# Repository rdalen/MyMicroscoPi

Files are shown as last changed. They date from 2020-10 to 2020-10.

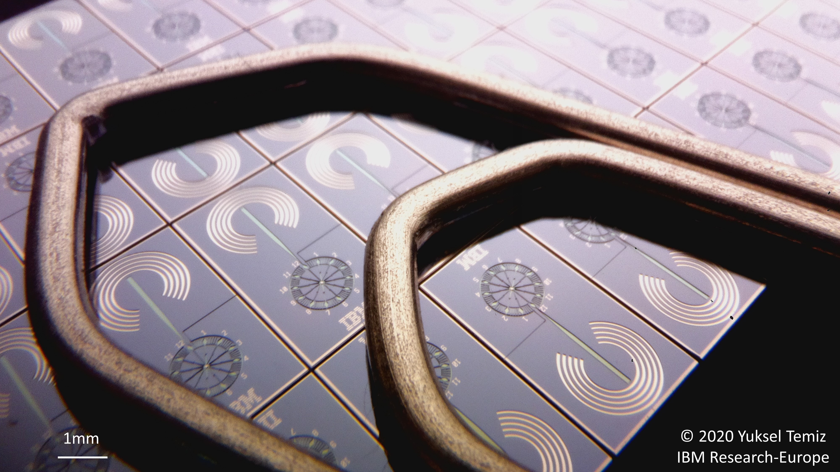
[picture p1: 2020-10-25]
Docs/Original/Image-examples/Microfluidic-clock_and_paper-clip.jpg

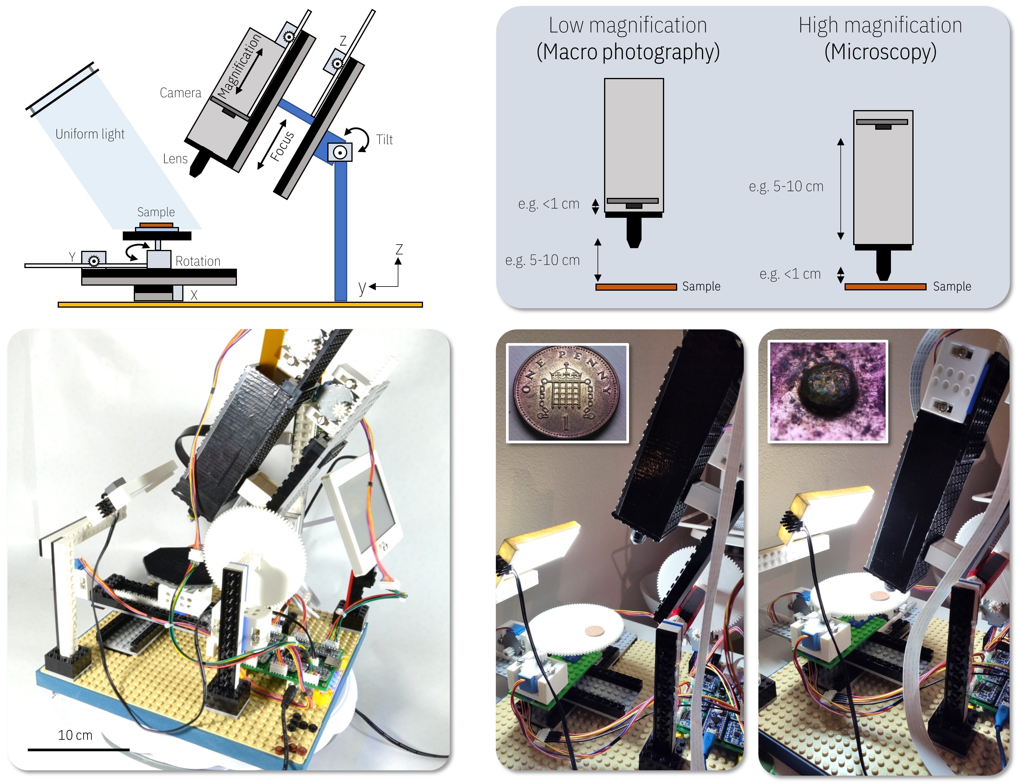
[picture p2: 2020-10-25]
Docs/Original/Pics/Operation.jpg

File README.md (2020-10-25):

# MyMicroscoPi
This DIY microscope design combines many of my hobbies; Lego, electronics, 3D printing, Arduino, Raspberry Pi, etc.

My design is a remix of a great and well documented [design of Yuksel Temizon](https://github.com/IBM/MicroscoPy).
My version is also built of LEGO bricks, but uses also LEGO Technic beams because they are light and strong.
For capturing images it uses a Raspberry Pi 3B+ with an 8MP camera and modified lens. The six stepper motors for the camera & sample movements and the power LED for illumination are controlled by two PCB's with an [Arduino Pro mini](https://www.arduino.cc/en/Guide/ArduinoProMini) on each PCB.
* One PCB (Mainboard) contains all the driver hardware for the steppers and power LED
* The other PCB (Controller board) contains the human interface elements for controlling the microscope. Such as; Three joysticks to control the X, Y, Rotary, Tilt (Camera-angle), Magnitude and Focus, a Rotary encoder to control the Power LED and a small OLED display to indicate the brightness of the power LED

I used the 3D printed LEGO gears and adapters of the [original design](https://github.com/IBM/MicroscoPy)

So, after many hours of building pleasure, I'm going to do some nice experiments now

### Information & Documentation
* [Hackster.io project; IBM Researcher Makes a Microscope Using LEGO, Arduino, and Raspberry Pi](https://www.hackster.io/news/ibm-researcher-makes-a-microscope-using-lego-arduino-and-raspberry-pi-cbc58cb69a20?utm_source=Hackster+Marketing&utm_campaign=7e2e7b20ec-EMAIL_CAMPAIGN_2019_02_14_02_53_COPY_01&utm_medium=email&utm_term=0_86d76c4d75-7e2e7b20ec-144680307&mc_cid=7e2e7b20ec&mc_eid=ea3c09e980)
* [Github IBM/MicroscoPy](https://github.com/IBM/MicroscoPy)
* [YouTube link MyMicroscoPi](https://youtu.be/3TL11zC14ig)

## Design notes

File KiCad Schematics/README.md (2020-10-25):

# KiCad
* Both PCB's are made with the version V1.0 design
* Modifications on these PCB's are incorporated in the version V2.0 schematics
* Hence; V2.0 has no PCB-update!!
* The gerber file of the Controllerboard V1.0 consists of a panel with 2 PCB's

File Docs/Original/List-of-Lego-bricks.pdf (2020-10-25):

List of Lego bricks used in the prototypes.

Some bricks may not be available in your country, but there are always alternative implementations in the world of Lego bricks. Also, there are probably many different ways of building a similar or better modules than I designed.
So, use your imagination and order extra bricks from different kinds in case you may want to modify something.

Keep in mind that some parts are required to be glued to a bigger piece for better mechanical stability.

I appreciate if you also keep in mind that this is a research prototype originated from my hobby, not a product.
There are probably many things that could have been done better, so consider the documents as a guideline but not as a product manual. Please let me know if you spot an error or have suggestions for improvements.

### https://www.lego.com/en-us/page/static/pick-a-brick

Module | Lego design name | Lego design ID | Quantity per unit | Quantity total | Purpose | Page # in the instructions | Comments
Base | 1 unit
| Baseplate 32x32 | | 1 | 1 | base | 32 | needs to be fixed to a rigid substrate
Linear actuators | 4 units
| PLATE 6X16 | 3027 | 1 | 4 | main plate for the linear stage | 5
| SLIDING PIECE 1X4 | 2653 | 8 | 32 | sliding guides on the sides | 5
| PLATE 1X2 WITH SLIDE | 32028 | 2 | 8 | sliding pieces | 7
| PLATE 2X4 | 3020 | 1 | 4 | moving plate | 7
| PLATE 2x6 | 3795 | 1 | 4 | mechanical stability | 6
| PLATE 6x8 | 3036 | 1 | 4 | motor plate | 6
| BRICK CORNER 1X2X2 | 2357 | 2 | 8 | mechanical stability | 6
| PLATE 2X4 | 3020 | 1 | 4 | motor Lego adapter | 9
Camera module | 1 unit | | | | | | in addition to one linear stage
| WALL ELEMENT 1X4X3, ABS | 60581 | 8 | 8 | sidewalls | 18
| PLATE 6X16 | 3027 | 1 | 1 | top cover | 19
| ANGLE PLATE 1X2 / 2X4 | 21731 | 1 | 1 | top cover connection | 19
| ANGULAR PLATE 1.5 BOT. 1X2 2/2 | 99207 | 1 | 1 | camera Lego adapter | 15
| PLATE 6x6 | 3958 | 1 | 1 | front cover | 19
| FRAME 1X4X3 | 60594 | 2 | 2 | Camera-Z connection spacer | 58
| PLATE 2X4 | 3020 | 1 | 1 | Camera-Z connection spacer | 57
Rotaty stage (option 1) | 1 unit
| 10x10 OCTOGONAL PLATE | 89523 | 1 | 1 | stage | 25
| PROFILE BRICK Ø15.83 W. CROSS | 92947 | 1 | 1 | connection to the motor | 25
| PLATE 2X4 | 3020 | 1 | 1 | motor Lego adapter | 25
Rotaty stage (option 2) | 1 unit | | | | | | preferred, better precision
| PLATE 4X12 | 3029 | 1 | 1 | stage base | 26
| LIGHT SWORD - BLADE | 21462 | 1 | 1 | pivot rod | 26
| NOSE CONE 2X2X2 | 14918 | 1 | 1 | support for the rod | 26
| PLATE 2X4 | 3020 | 1 | 1 | mechanical stability | 26
| PLATE 2X4 | 3020 | 1 | 1 | motor Lego adapter | 25
Vertical supports | 3 units | | | | | | tilt mechanism and illumination
| BRICK 1X16 | 2465 | 2 | 6 | pillar | 30
| PLATE 2X16 | 4282 | 1 | 3 | pillar | 30
| FRAME PLATE 4X4 | 64799 | 1 | 3 | pillar support | 30
| ANGULAR PLATE 1.5 BOT. 1X2 2/2 | 99207 | 1 | 3 | connection | 30
| BRICK CORNER 1X2X2 | 2357 | 4 | 12 | connection | 30
| PLATE 1X4 | 3710 | 4 | 12 | connection | 30
| PLATE 1x2 | 3023 | 4 | 12 | connection | 30
Tilt mechanism | 1 unit
| TECHNIC BRICK 1X2, Ø4.9 | 3700 | 2 | 2 | camera stage | 31
| CONN.BUSH W.FRIC./CROSSALE | 43093 | 2 | 2 | camera stage | 31
| PLATE 2X8 | 3034 | 2 | 2 | camera stage | 31
| BRICK 2X6 | 44237 | 1 | 1 | camera stage | 31
| PLATE 2X4 | 3020 | 3 | 3 | mechanical stability | 34-37
| PLATE 2X4 | 3020 | 1 | 1 | motor Lego adapter | 34-37
| PROFILE BRICK Ø15.83 W. CROSS | 92947 | 5 | 5 | spacer | 34-37
| TURN PLATE 2X2, LOWER PART | 3680 | 2 | 2 | rotation | 34-37
| TURN PLATE 2X2, UPPER PART | 3679 | 2 | 2 | rotation | 34-37
Illumination | 1 unit | | | | | | in addition to one vertical support
| CONN.BUSH W.FRIC./CROSSALE | 43093 | 4 | 4 | connection to the stage | 42-44 | for bottom illumination
| BRICK 1X16 | 2465 | 2 | 2 | horizontal connection | 43
| PLATE 2X16 | 4282 | 1 | 1 | horizontal connection | 43
| BRICK 2X2 W. BALL Ø 10.2 | 57909 | 1 | 1 | hinge | 43 | for top illumination
| BRICK 2X2 W. CUP FOR BALL | 92013 | 1 | 1 | hinge | 43 | for top illumination

OPTIONAL
HQ camera (experimental) | 1 unit | | | | | | Optional. Refer to the Instructions_HQ.pdf
linear actuator | PLATE 8x16 | 92438 | 1 | 1 | main plate | 4
linear actuator | PLATE 6x8 | 3036 | 1 | 1 | motor plate | 4
linear actuator | PLATE 2x8 | 3034 | 1 | 1 | mechanical stability | 4
linear actuator | PLATE 2x6 | 3795 | 1 | 1 | moving plate | 4 | same as camera v2
linear actuator | PLATE 1X2 WITH SLIDE | 32028 | 2 | 2 | sliding pieces | 4 | same as camera v2
linear actuator | BRICK CORNER 1X2X2 | 2357 | 2 | 2 | mechanical stability | 4 | same as camera v2
linear actuator | PLATE 2X4 | 3020 | 1 | 1 | motor Lego adapter | 4 | same as camera v2
linear actuator | SLIDING PIECE 1X4 | 2653 | 8 | 8 | sliding guides on the sides | 4 | same as camera v2
camera module | ANGULAR PLATE 1.5 BOT. 1X2 2/2 | 99207 | 1 | 1 | camera Lego adapter | 6 | same as camera v2
camera module | PLATE W. BOW 2X2X2/3 | 15068 | 1 | 1 | mechanical stability | 7
camera module | WALL ELEMENT 1X4X3, ABS | 60581 | 8 | 8 | sidewalls | 9 | same as camera v2
camera module | BRICK 1X16 | 2465 | 4 | 4 | additional height | 9
camera module | ANGLE PLATE 1X2 / 2X4 | 21731 | 1 | 1 | top cover connection | 10 | same as camera v2
camera module | PLATE 8X16 | 92438 | 1 | 1 | top cover | 10
camera module | PLATE 8X8 | 41539 | 1 | 1 | front cover | 10
tilt mechanism | PLATE 4X8 | 3035 | 2 | 2 | camera stage top and bottom plate | 13 | wider stage
tilt mechanism | TECHNIC BRICK 1X2, Ø4.9 | 3700 | 2 | 2 | camera stage | 13 | same as camera v2
tilt mechanism | CONN.BUSH W.FRIC./CROSSALE | 43093 | 2 | 2 | camera stage | 13 | same as camera v2
tilt mechanism | BRICK 1X8 | 3008 | 2 | 2 | camera stage | 13
tilt mechanism | PLATE 2X6 | 3795 | 1 | 1 | camera stage | 13

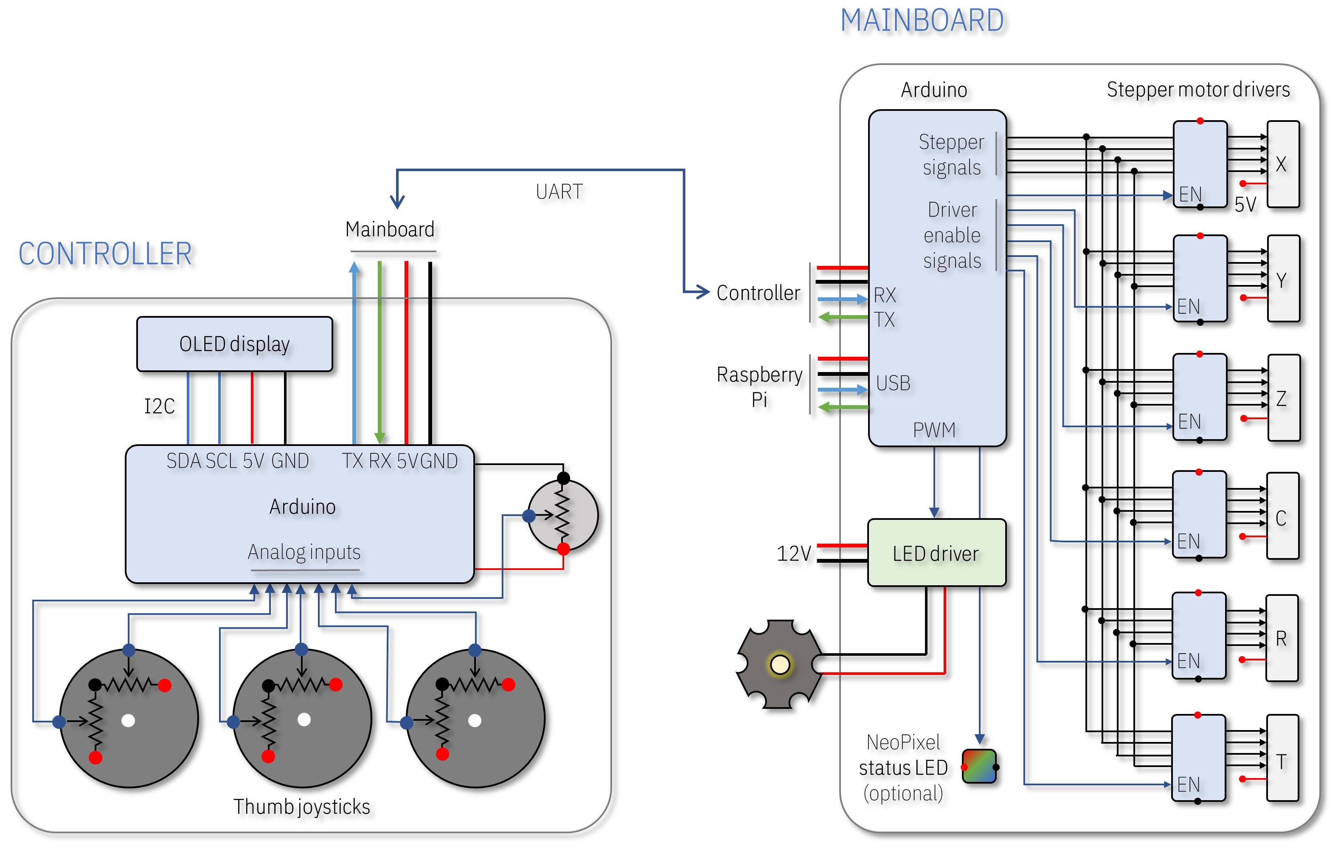
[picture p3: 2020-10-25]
Docs/Original/Pics/Electronics.jpg

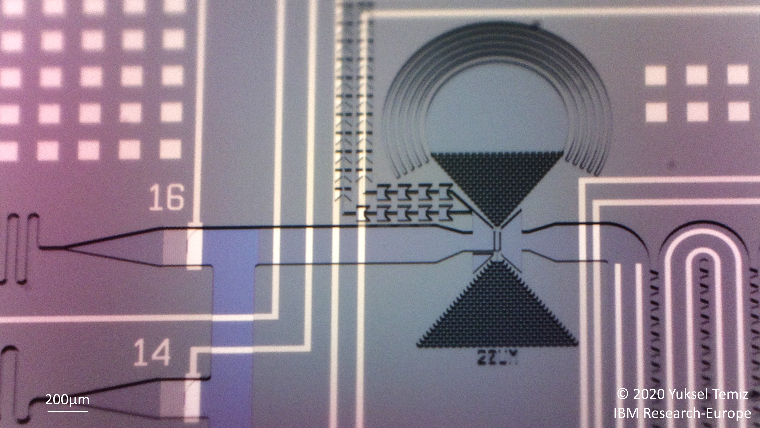
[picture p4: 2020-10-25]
Docs/Original/Image-examples/Microfluidic-structures.jpg

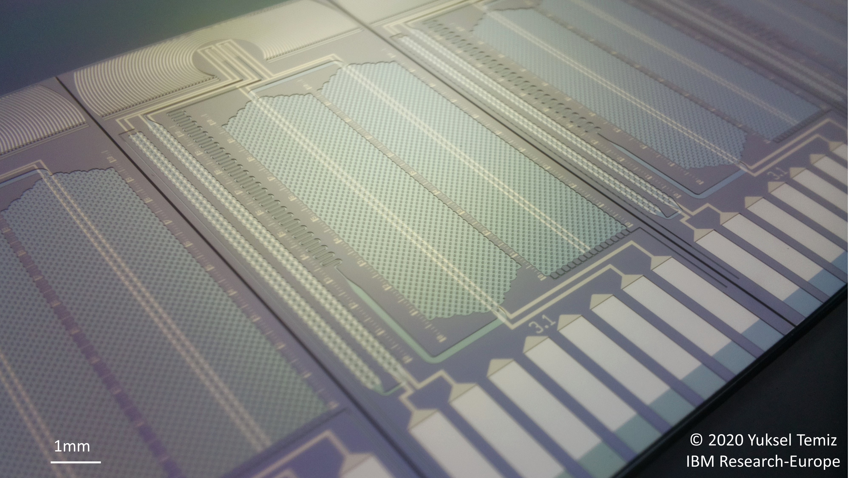
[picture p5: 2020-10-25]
Docs/Original/Image-examples/Microfluidic-chip.jpg

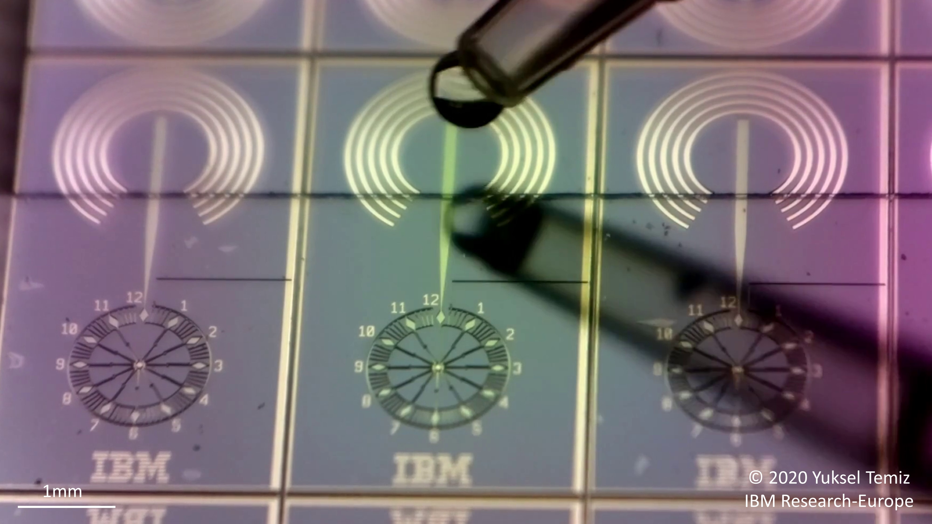
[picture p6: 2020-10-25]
Docs/Original/Image-examples/Microfluidic_clock.jpg

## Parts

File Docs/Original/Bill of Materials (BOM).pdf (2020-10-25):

# Bill of materials

Item | Total price ($) | Remarks
LEGO bricks (https://www.lego.com/en-us/page/static/pick-a-brick) | ~60 | I recommend buying extra bricks in different sizes.
Raspberry Pi (https://www.raspberrypi.org/products/) | 10-50 | Any model works.
Raspberry Pi camera (https://www.raspberrypi.org/products/camera-module-v2/) | 25
Camera flex cable (https://www.adafruit.com/product/1731) | 3 | A long cable (>40cm) is preferred if the Raspberry Pi cannot be placed closer to the camera.
Magnifying lens (https://www.aliexpress.com/i/32879460954.html) | 10 | M12 thread
Micro SD card (https://www.raspberrypi.org/documentation/installation/sd-cards.md) | 10 | Raspberry Pi operating system. Minimum 16GB is recommended.
HDMI display (https://www.adafruit.com/product/2260) | 50-150 | Optional if an HDMI display is already available. The price varies depending on the size and the model.
Arduino board (https://www.adafruit.com/product/3677) x2 | 20 | One for the mainboard, one for the controller. Any Arduino board with enough number of IO pins should work.
Stepper motor driver (https://www.adafruit.com/product/3297) x6 | 30 | Any other 5V compatible driver should work. Microstepping was not needed in this project.
Stepper motor (https://www.banggood.com/28BYJ-48-5V-4-Phase-DC-Gear-Stepper-Motor-DIY-Kit-p-1553617.html?rmmds=search&cur_warehouse=CN) x6 | 15 | 28BYJ-48, 5V, 1/64 gear ratio
JST-XH 5P 4S cables (https://www.ebay.com/itm/JST-XH-5P-4S-Li-PO-Balance-Charging-Wire-Extension-22AWG-20cm-Adapter-Lead-x-5/122329707748) | 7 | A few of these cables are required the extend the default cable of the stepper motor (28BYJ-48)
High-power LED (https://www.digikey.com/products/en?keywords=1672-1161-ND) | 4
High-power LED driver (https://www.digikey.com/products/en?keywords=945-1818-5-ND) | 14
Light diffuser (https://www.adafruit.com/product/1621) | 3 | An LED backlight module is modified by replacing the low-power LED by a high-power one
Potentiometer (https://www.adafruit.com/product/4133) | 1 | LED intensity control using pulse-width modulation.
Thumb joysticks (https://www.sparkfun.com/products/9032) x3 | 12 | Three joysticks for X, Y, Z, Camera, Tilt, and Rotation.
5V power supply (https://www.raspberrypi.org/products/type-c-power-supply/) | 20 | At least 3A is preferred. A more powerful supply may be needed if the display is also powered from the same supply.
DC-DC converter (https://www.banggood.com/DC-DC-Boost-Buck-Adjustable-Step-Up-Step-Down-Automatic-Converter-XL6009-Module-p-1087346.html?rmmds=search&cur_warehouse=CN) | 3 | In case the LED and its driver require more than 5V.
OLED display (https://www.banggood.com/0_91-Inch-128x32-IIC-I2C-Blue-OLED-LCD-Display-DIY-Oled-Module-SSD1306-Driver-IC-DC-3_3V-5V-p-1140506.html?rmmds=search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) | 3 | Displays the LED intensity or any other information on the controller.
USB connector (https://www.digikey.com/products/en?keywords=UE27AC5410H-ND) (type A) | 0.5 | Connection between the mainboard and the controller (mainboard side).
USB connector (https://www.digikey.com/products/en?keywords=609-4616-1-ND) (micro) | 0.5 | Connection between the mainboard and the controller (controller side).
JST XH connector set (https://www.banggood.com/40-Sets-JST-2_5mm-XH-2P-3P-4P-5Pin-Male-Female-Housing-Connector-with-Crimps-p-1180083.html?rmmds=search&cur_warehouse=CN) | 5 | Connectors for the stepper motors and the LED
DC barrel connector (https://www.sparkfun.com/products/119) | 1 | In case a separate DC input (e.g. 12V) is needed for the LED
OVERALL TOTAL | ~300

## - The prices and the links are for exemplary components that

were used in this prototype.

## - Any other compatible model

should work in principle.

## - The total price varies significantly depending on the vendor and the model. For example, the type of the Raspberry Pi and the display makes a big difference in the

price.

## - The cost of 3D-printed parts is

not included.

## - There are also a few other accessories needed, like USB

cables, an HDMI cable,

## optionally a mouse and a

keyboard, an ON/OFF switch,

## screws and nuts, and printed

circuit boards (PCBs).

IBM Research - Zurich | Images © 2020 Yuksel Temiz

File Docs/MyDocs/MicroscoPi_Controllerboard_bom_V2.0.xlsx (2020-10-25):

Component | References | Value | Quantity | Part | Description | Footprint | Datasheet | Field4 | Price/piece | Price Total
1 | A1 | Arduino_Pro_mini | 1 | Arduino_Pro_mini | Arduino Pro Mini | Arduino_pro_mini_v2 | https://www.evernote.com/l/AD4DRM0B5n5O7J_GKryOX0b1Ho4iJdDhcCU/ |  | 1.99 | 1.99
2 | C1 C2 | 100nF | 2 | C | Unpolarized capacitor | C_Rect_L7.0mm_W3.5mm_P2.50mm_P5.00mm | ~ |  | 0.01 | 0.02
3 | J1 | I2C (for testing purpose) | 1 | Conn_01x04_Female | Generic connector, single row, 01x04, script generated (kicad-library-utils/schlib/autogen/connector/) | PinSocket_1x04_P2.54mm_Vertical | ~ |  | 0.04 | 0.04
4 | J3 | Power in | 1 | USB_B_Micro | USB Micro Type B connector | USB_Micro-B_Molex-105017-0001 | https://www.evernote.com/shard/s62/sh/747e80cf-da2d-4e95-b6d8-e3c64d316c75/671090d3e83537ea649cd51a3a3a36f9 |  | 0.08 | 0.08
7 | SW1 | Rotary_Encoder_Switch | 1 | Rotary_Encoder_Switch | Rotary encoder, dual channel, incremental quadrate outputs, with switch | RotaryEncoder_Alps_EC11E-Switch_Vertical_H20mm | https://www.evernote.com/l/AD6MthjFr_VGQb9QrLRkJV6A4uxv8JMFLmg/ |  | 0.40 | 0.40
8 | U4 | Display_I2C_OLED | 1 | Display_I2C_OLED | Display OLED 128x64 0.91" I2C | SSD1306_OLED-0.91-128x32 | https://www.evernote.com/l/AD62jUmcMJBGZpAa-3Ric2js8dKCUVTVpok/ | 128x32 | 1.69 | 1.69
9 | U1 U2 U3 | JOYSTICK_BUTTON | 3 | JOYSTICK_BUTTON |  | Joystick_w_Button | https://www.evernote.com/l/AD6xE7tqk31F_41CDl8qYf35tWgwOpIksp4/ |  | 1.18 | 3.53
 |  |  |  | PCB |  |  |  |  | 1.69 | 0.85
5 | L2 | Logo-RvD | 1 | Logo-RvD |  | RvD Logo inverted small
6 | L1 | Logo-TechDen | 1 | Logo-TechDen |  | TechDen Logo - inverted
 |  |  |  |  |  |  |  |  |  | 8.59 | Total
Component Groups: | 9
Component Count: | 12
Fitted Components: | 12
Number of PCBs: | 1
Total components: | 12
Schematic Version: | V2.0
Schematic Date: | 2020-10-02
BoM Date: | 25/10/2020 14:42:16
Schematic Source: | C:\Users\Roland enof Anita\Dropbox\MyKiCad\MySchematics\MicroscoPi\MicroscoPi_Controllerboard\v2.0\MicroscoPi_Controllerboard.sch
KiCad Version: | Eeschema (5.1.5)-3

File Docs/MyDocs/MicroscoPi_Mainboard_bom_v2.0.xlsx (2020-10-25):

Component | References | Value | Quantity | Part | Description | Footprint | Datasheet | Text1 | Text2 | Field7 | Text3 | Price/piece | Price Total
1 | A2 | Arduino_Pro_mini | 1 | Arduino_Pro_mini | Arduino Pro Mini | Arduino_pro_mini_v2 | https://www.evernote.com/l/AD4DRM0B5n5O7J_GKryOX0b1Ho4iJdDhcCU/ |  |  |  |  | 1.99 | 1.99
2 | A3 | StepperC | 1 | Adafruit_Breakout_DRV8825 | Adafruit Breakout Board, Stepper Driver DRV8825 | Adafruit_Breakout_DRV8825 | https://learn.adafruit.com/adafruit-drv8833-dc-stepper-motor-driver-breakout-board/overview |  |  |  |  | 2.35 | 2.35
3 | A6 | StepperR | 1 | Adafruit_Breakout_DRV8825 | Adafruit Breakout Board, Stepper Driver DRV8825 | Adafruit_Breakout_DRV8825 | https://learn.adafruit.com/adafruit-drv8833-dc-stepper-motor-driver-breakout-board/overview |  |  |  |  | 2.35 | 2.35
4 | A7 | StepperT | 1 | Adafruit_Breakout_DRV8825 | Adafruit Breakout Board, Stepper Driver DRV8825 | Adafruit_Breakout_DRV8825 | https://learn.adafruit.com/adafruit-drv8833-dc-stepper-motor-driver-breakout-board/overview |  |  |  |  | 2.35 | 2.35
5 | A1 | StepperX | 1 | Adafruit_Breakout_DRV8825 | Adafruit Breakout Board, Stepper Driver DRV8825 | Adafruit_Breakout_DRV8825 | https://learn.adafruit.com/adafruit-drv8833-dc-stepper-motor-driver-breakout-board/overview |  |  |  |  | 1.75 | 1.75
6 | A4 | StepperY | 1 | Adafruit_Breakout_DRV8825 | Adafruit Breakout Board, Stepper Driver DRV8825 | Adafruit_Breakout_DRV8825 | https://learn.adafruit.com/adafruit-drv8833-dc-stepper-motor-driver-breakout-board/overview |  |  |  |  | 1.75 | 1.75
7 | A5 | StepperZ | 1 | Adafruit_Breakout_DRV8825 | Adafruit Breakout Board, Stepper Driver DRV8825 | Adafruit_Breakout_DRV8825 | https://learn.adafruit.com/adafruit-drv8833-dc-stepper-motor-driver-breakout-board/overview |  |  |  |  | 1.75 | 1.75
 |  | JST connectors | 6 | Adafruit_Breakout_DRV8825 | Adafruit Breakout Board, Stepper Driver DRV8825 | Adafruit_Breakout_DRV8825 | https://learn.adafruit.com/adafruit-drv8833-dc-stepper-motor-driver-breakout-board/overview |  |  |  |  | 0.04 | 0.22
 |  | Cables | 5 | Adafruit_Breakout_DRV8825 | Adafruit Breakout Board, Stepper Driver DRV8825 | Adafruit_Breakout_DRV8825 | https://learn.adafruit.com/adafruit-drv8833-dc-stepper-motor-driver-breakout-board/overview |  |  |  |  | 0.79 | 3.96
8 | C1 C2 C3 C4 C5 C6 C7 | 100nF | 7 | C | Unpolarized capacitor | C_Rect_L7.0mm_W3.5mm_P2.50mm_P5.00mm | ~ |  |  |  |  | 0.01 | 0.07
9 | D1 D2 D3 D4 D5 D6 D7 D8 D9 D10 D11 D12 | DUS | 12 | 1N4148 | 100V 0.15A standard switching diode, DO-35 | D_DO-35_SOD27_P7.62mm_Horizontal | https://assets.nexperia.com/documents/data-sheet/1N4148_1N4448.pdf |  |  |  |  | 0.01 | 0.12
10 | D13 | WS2812B | 1 | WS2812B | RGB LED with integrated controller | LED_WS2812B_PLCC4_5.0x5.0mm_P3.2mm | https://cdn-shop.adafruit.com/datasheets/WS2812B.pdf |  |  |  |  | 0.23 | 0.23
11 | J2 J4 J5 J8 J9 J12 J15 J16 | EndstopX | 8 | Conn_01x03_Male | Generic connector, single row, 01x03, script generated (kicad-library-utils/schlib/autogen/connector/) | PinHeader_1x03_P2.54mm_Vertical | (Active HIGH) |  |  |  |  | 1.06 | 6.35
12 | J18 | Power Jack | 1 | Barrel_Jack_Switch | DC Barrel Jack with an internal switch | BarrelJack_Horizontal | ~ | +5Vdc input |  |  |  | 0.15 | 0.15
13 | J17 | Power LED 3W (1A) | 1 | Conn_01x02_Male | Generic connector, single row, 01x02, script generated (kicad-library-utils/schlib/autogen/connector/) | PhoenixContact_GMSTBVA_2,5_2-G-7,62_1x02_P7.62mm_Vertical | ~ |  |  |  |  | 1.20 | 1.20
 |  | Backlight Module | 1 |  |  |  |  |  |  |  |  | 8.15 | 8.15
 |  | heat sink | 1 |  |  |  |  |  |  |  |  | 1.35 | 1.35
14 | J1 J3 J6 J7 J10 J11 | StepperX | 6 | Conn_01x05_Male | Generic connector, single row, 01x05, script generated (kicad-library-utils/schlib/autogen/connector/) | JST_XH_B5B-XH-A_1x05_P2.54mm_Vertical | 28BYJ-48 5V 1/64 reduction Step Motor |  |  |  |  | 1.78 | 10.70
15 | J14 | from RPI | 1 | USB_B_Micro | USB Micro Type B connector | USB_Micro-B_Molex-105017-0001 | https://www.evernote.com/shard/s62/sh/747e80cf-da2d-4e95-b6d8-e3c64d316c75/671090d3e83537ea649cd51a3a3a36f9 |  |  |  |  | 0.08 | 0.08
16 | J13 | to Controller | 1 | USB_A | USB Type A connector | USB_A_Stewart_SS-52100-001_Horizontal | https://www.evernote.com/l/AD6pv4W2eFFAQI7Wvrlgkl1mAzs7RMjzu9o/ |  |  |  |  | 0.18 | 0.18
17 | JP1 | Vcc | 1 | SolderJumper_2_Open | Solder Jumper, 2-pole, open | SolderJumper-2_P1.3mm_Open_Pad1.0x1.5mm | ~
18 | L2 | Logo-RvD | 1 | Logo-RvD |  | RvD Logo inverted small
19 | L1 | Logo-TechDen | 1 | Logo-TechDen |  | TechDen Logo - inverted
20 | R2 | 470E | 1 | R | Resistor | R_Axial_DIN0207_L6.3mm_D2.5mm_P10.16mm_Horizontal | ~ |  |  |  |  | 0.01 | 0.01
21 | R1 | 4k7 | 1 | R | Resistor | R_Axial_DIN0207_L6.3mm_D2.5mm_P10.16mm_Horizontal | ~ |  |  |  |  | 1.01 | 1.01
22 | U1 | LD48AJTA | 1 | LD48AJTA | LED Driver 1A Dimmable | LD48AJTA | https://www.evernote.com/l/AD601X_BTF5HHI8A9-_ns2xVQMNyB5-bSGo/ | LED Driver 1A |  |  |  | 3.44 | 3.44
23 | U2 | XW-0511-12-24W | 1 | XW-0511-12-24W | Non isolated dc-dc converter step-up 5-11Vdc input 12Vdc output | XW-0511-12-24W | https://www.evernote.com/l/AD6jBATxN1VKd58cuCVOaBLS35bOezNZF28/ | DC-DC Converter | 5-11Vdc | VERVALLEN | 12Vdc
 |  | Power adapter 5Vdc & 12Vdc | 1 |  |  |  |  |  |  |  |  | 12.96 | 12.96
 |  | PCB | 1 |  |  |  |  |  |  |  |  | 1.69 | 1.69
 |  |  |  |  |  |  |  |  |  |  |  |  | 66.17 | Total
 | Further
 |  | Raspberry Pi 3B+ | 1 |  |  |  |  |  |  |  |  |  | 33.01
 |  | RPI Camera Module V2 8MP | 1 |  |  |  |  |  |  |  |  |  | 24.75
 |  | magnifying lens | 1 |  |  |  |  |  |  |  |  |  | 9.97
 |  | Flexkabel Camera - 45cm |  |  |  |  |  |  |  |  |  |  | 5.45
 |  |  |  |  |  |  |  |  |  |  |  |  | 73.18
 | and | Div Lego
Component Groups: | 23
Component Count: | 52
Fitted Components: | 52
Number of PCBs: | 1
Total components: | 52
Schematic Version: | v2.0
Schematic Date: | 2020-10-02
BoM Date: | 25/10/2020 14:43:34
Schematic Source: | C:\Users\Roland enof Anita\Dropbox\MyKiCad\MySchematics\MicroscoPi\MicroscoPi_Mainboard\v2.0\MicroscoPi_Mainboard.sch
KiCad Version: | Eeschema (5.1.5)-3

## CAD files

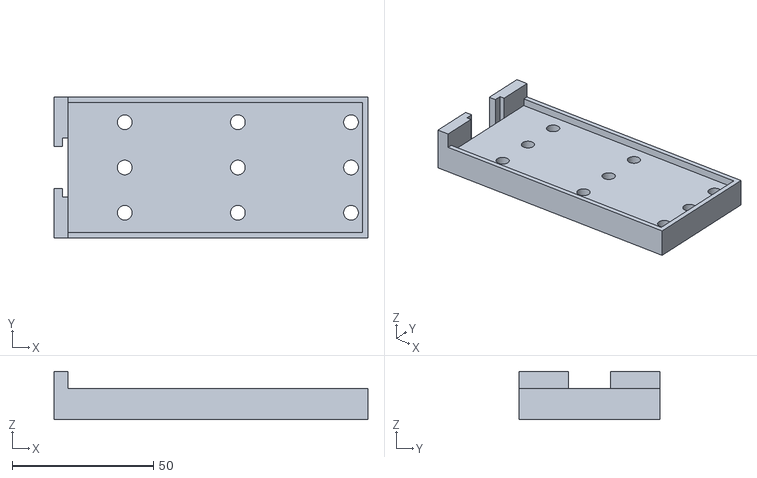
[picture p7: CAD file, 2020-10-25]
3D-design-files/09-LEDhousing.stl
111.0 x 50.0 x 17.0

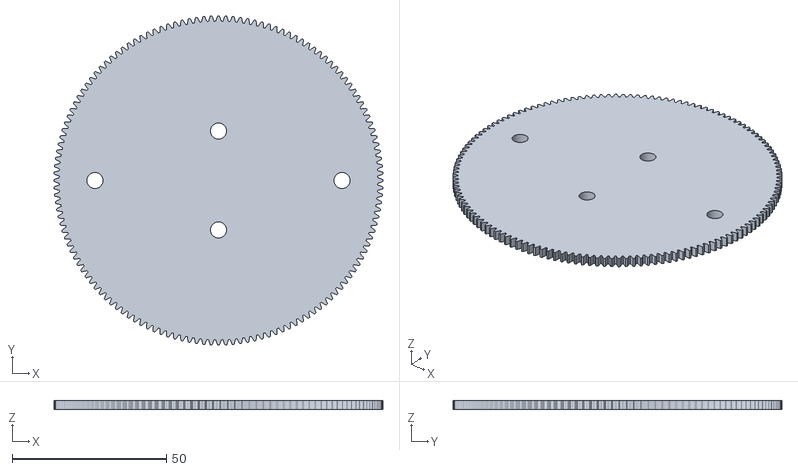
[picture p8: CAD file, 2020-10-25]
3D-design-files/07-RotationGear.stl
106.5 x 106.5 x 3.00

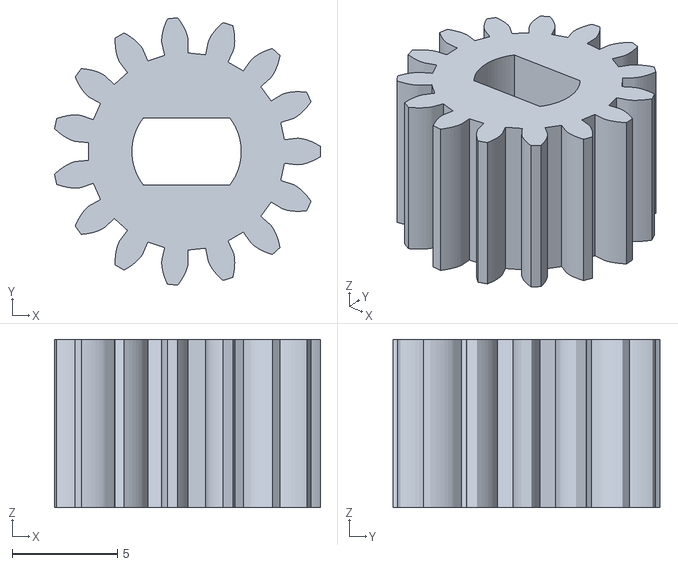
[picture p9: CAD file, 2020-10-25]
3D-design-files/02-MotorGear.stl
12.7 x 12.7 x 8.00

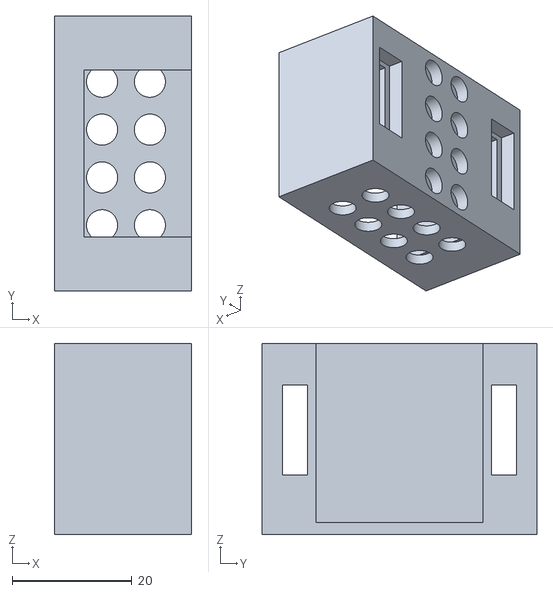
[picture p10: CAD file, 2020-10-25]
3D-design-files/03-MotorHousing.stl
23.0 x 46.0 x 32.0

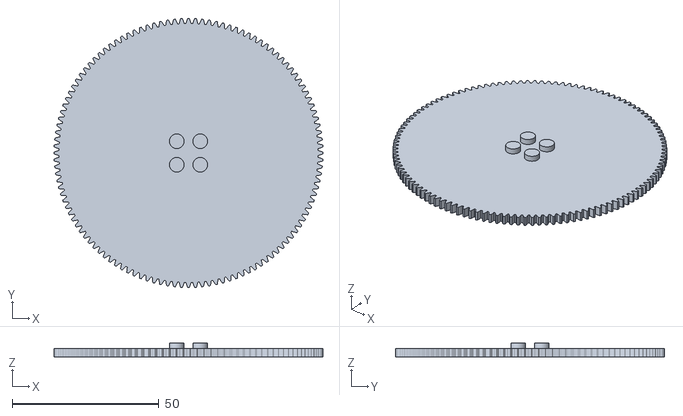
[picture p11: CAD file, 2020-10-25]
3D-design-files/08-TiltGear.stl
91.5 x 91.5 x 4.90

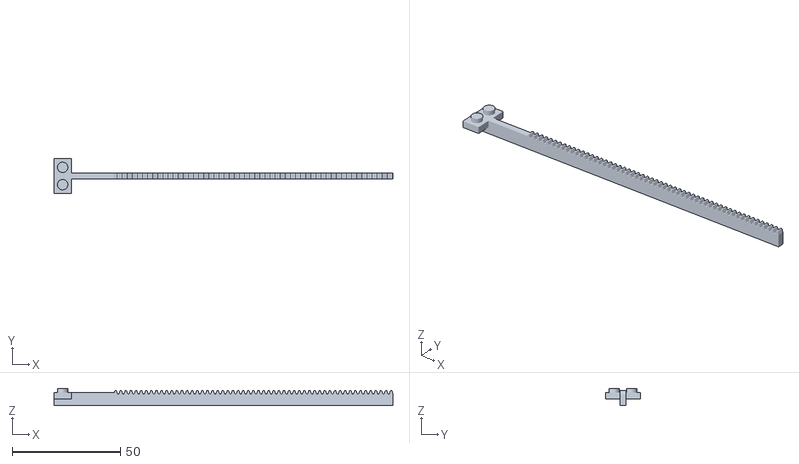
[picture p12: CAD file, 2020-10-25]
3D-design-files/01-RackGear.stl
156.6 x 16.0 x 8.00

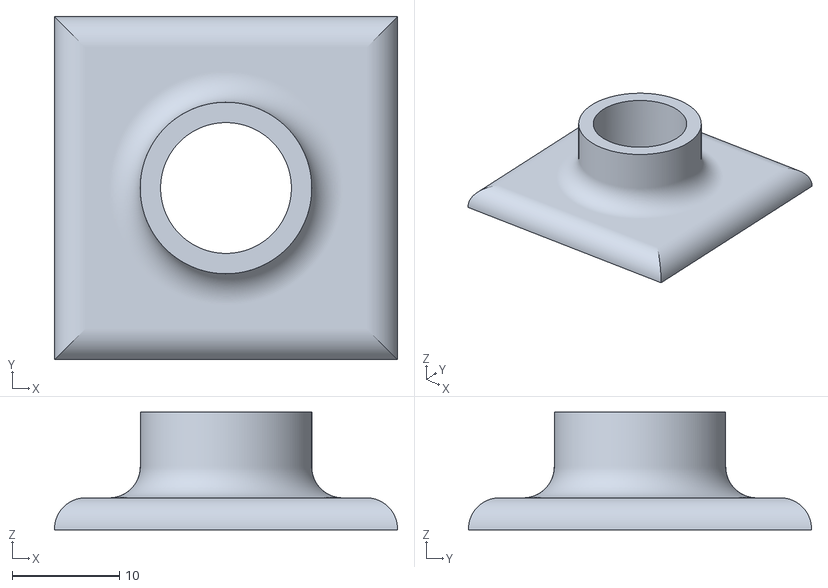
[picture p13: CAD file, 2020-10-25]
3D-design-files/05-LensAdapter.stl
32.0 x 32.0 x 11.0

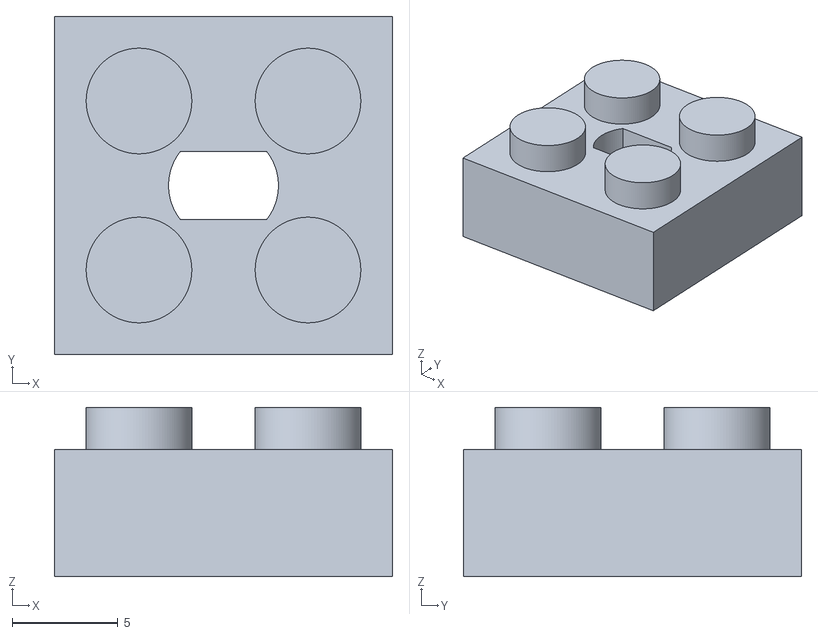
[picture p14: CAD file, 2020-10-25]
3D-design-files/06-ShaftAdapter.stl
16.0 x 16.0 x 8.00

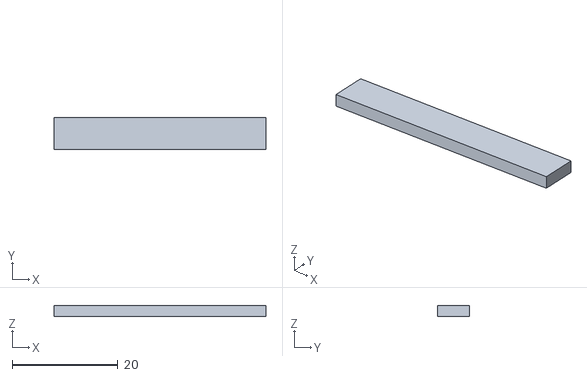
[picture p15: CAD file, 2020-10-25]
3D-design-files/10-LEDfixture.stl
40.0 x 6.00 x 2.00

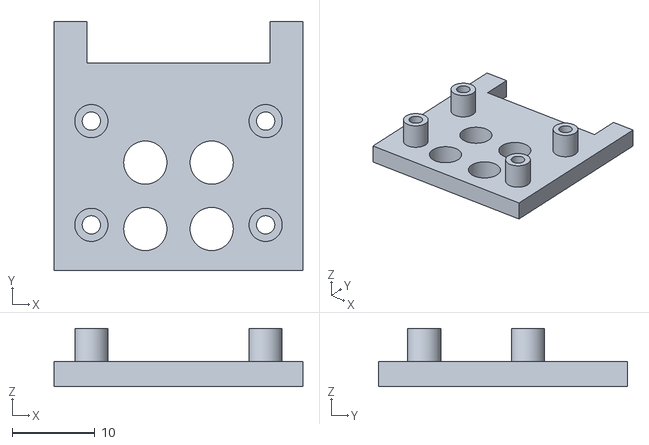
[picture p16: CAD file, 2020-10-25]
3D-design-files/04-CameraAdapter.stl
30.0 x 30.0 x 7.00

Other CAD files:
3D-design-files/08-TiltGear_with_hole.stl

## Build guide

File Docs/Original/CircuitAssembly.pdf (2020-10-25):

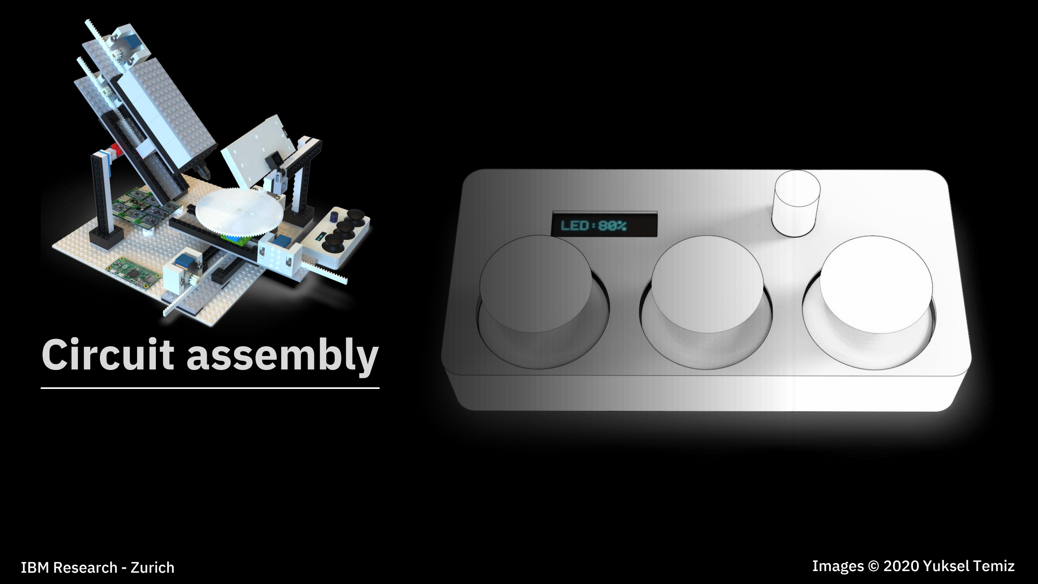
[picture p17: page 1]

# Circuit assembly

IBM Research - Zurich | Images © 2020 Yuksel Temiz

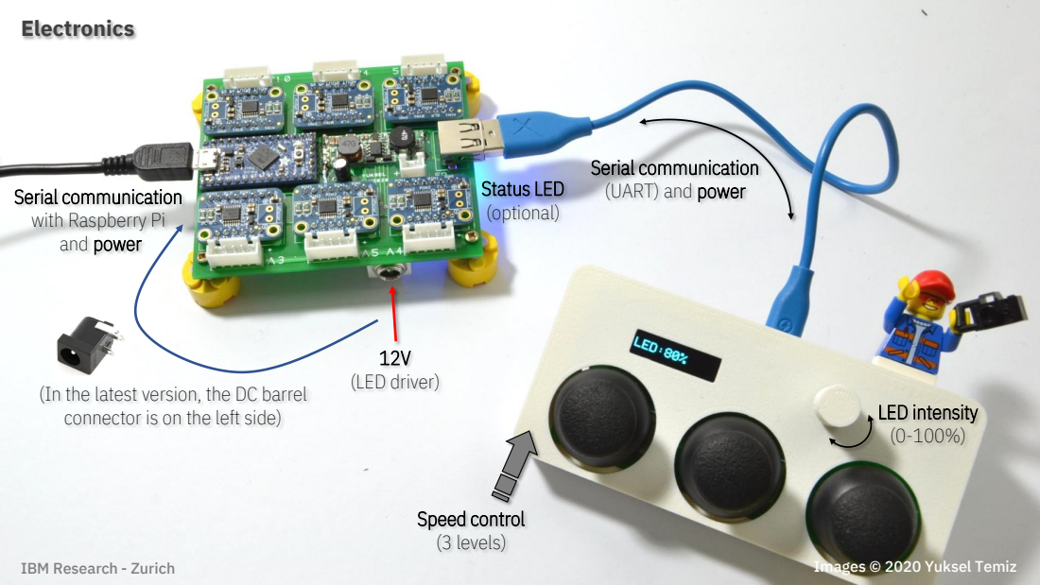
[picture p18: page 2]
Electronics; 12V (LED driver); Speed control (3 levels); LED intensity (0-100%); Status LED (optional)

Serial communication
(UART) and power

with Raspberry Pi
and power

(In the latest version, the DC barrel
connector is on the left side)

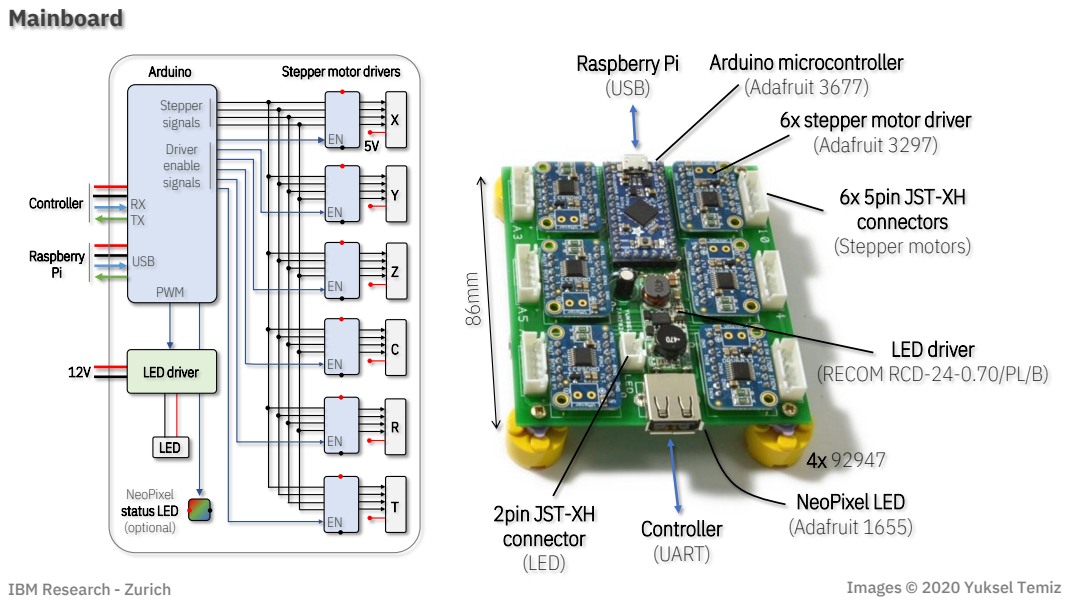
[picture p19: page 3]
Mainboard; 6x 5pin JST-XH connectors (Stepper motors); LED driver; Controller (UART); 2pin JST-XH connector (LED); NeoPixel LED (Adafruit 1655); Controller; Raspberry Pi; LED; Stepper signals; Driver enable signals; Arduino; USB; PWM; NeoPixel status LED (optional); Raspberry Pi (USB)

Arduino microcontroller
(Adafruit 3677)
6x stepper motor driver
(Adafruit 3297)

Stepper motor drivers

(RECOM RCD-24-0.70/PL/B)

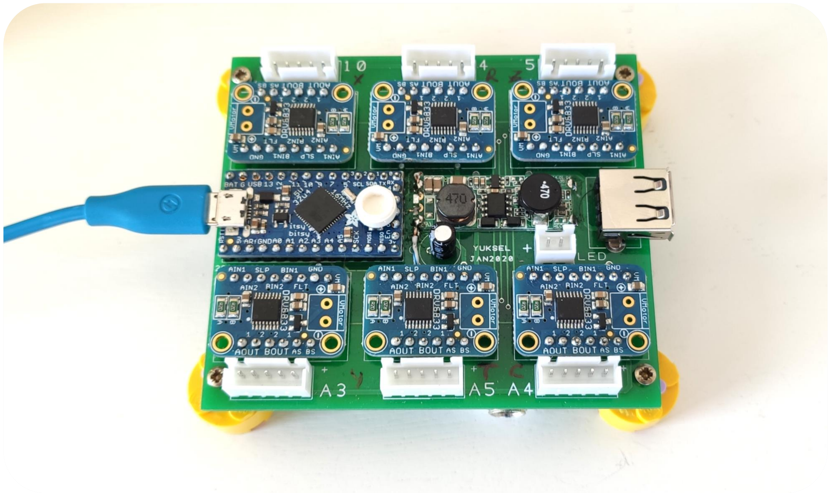
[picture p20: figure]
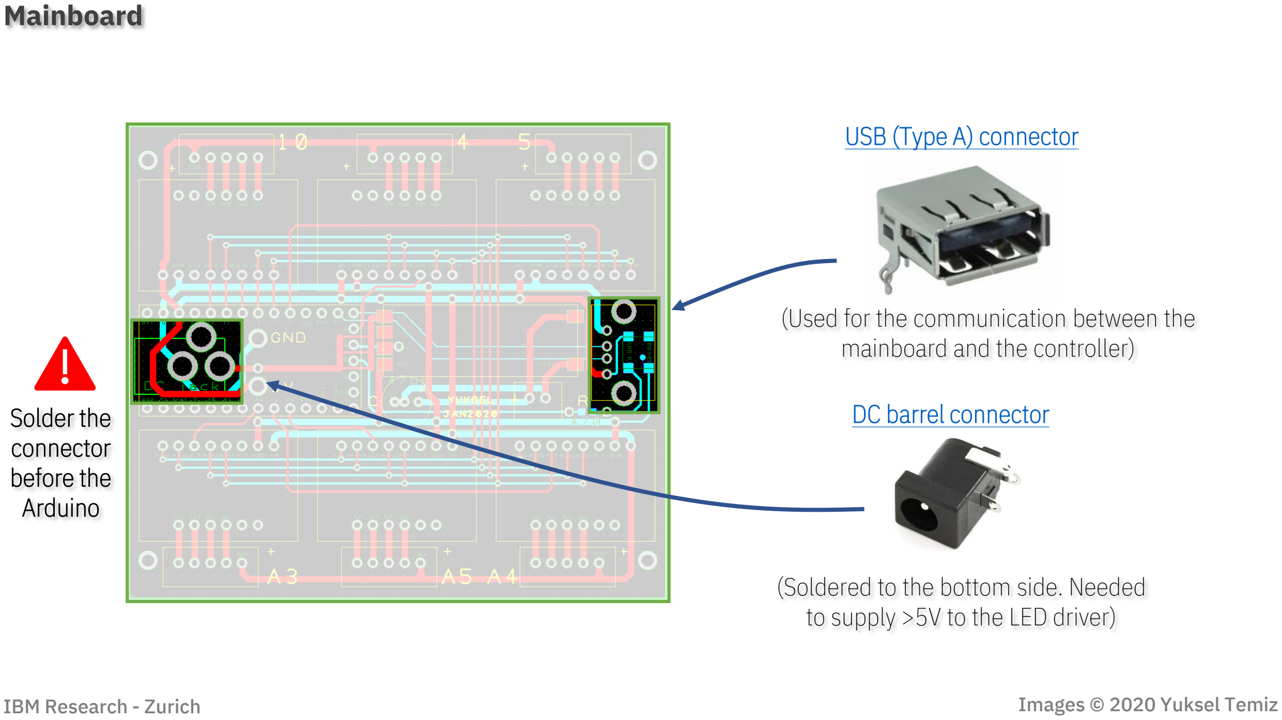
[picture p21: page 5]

(Used for the communication between the mainboard and the controller)

USB (Type A) connector (https://www.digikey.com/products/en?keywords=UE27AC5410H-ND)

DC barrel connector (https://www.sparkfun.com/products/119)

(Soldered to the bottom side. Needed to supply >5V to the LED driver)

Solder the
connector
before the
Arduino

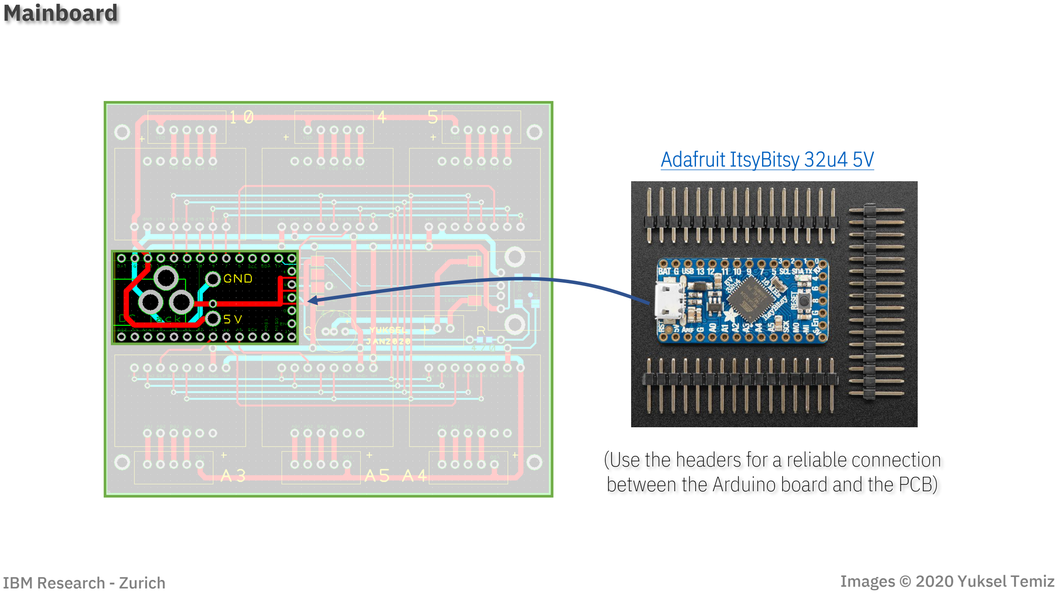
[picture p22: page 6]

Adafruit ItsyBitsy 32u4 5V (https://www.adafruit.com/product/3677)

(Use the headers for a reliable connection between the Arduino board and the PCB)

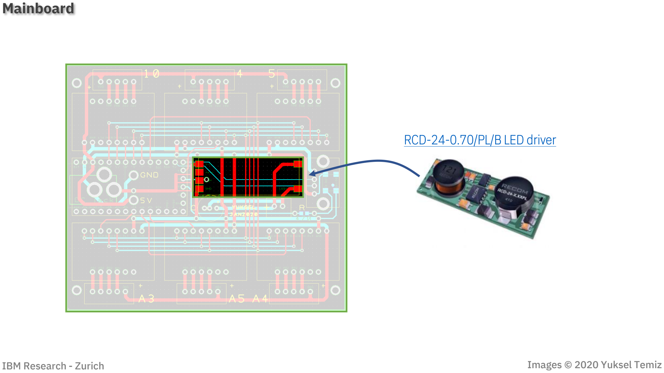
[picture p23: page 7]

RCD-24-0.70/PL/B LED driver (https://www.digikey.com/products/en?keywords=945-1818-5-ND)

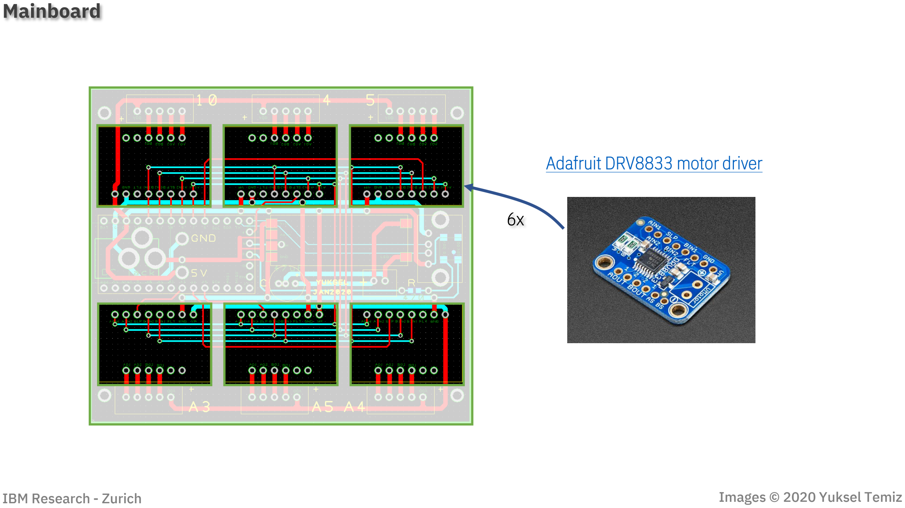
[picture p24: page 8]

Adafruit DRV8833 motor driver (https://www.adafruit.com/product/3297)

6x

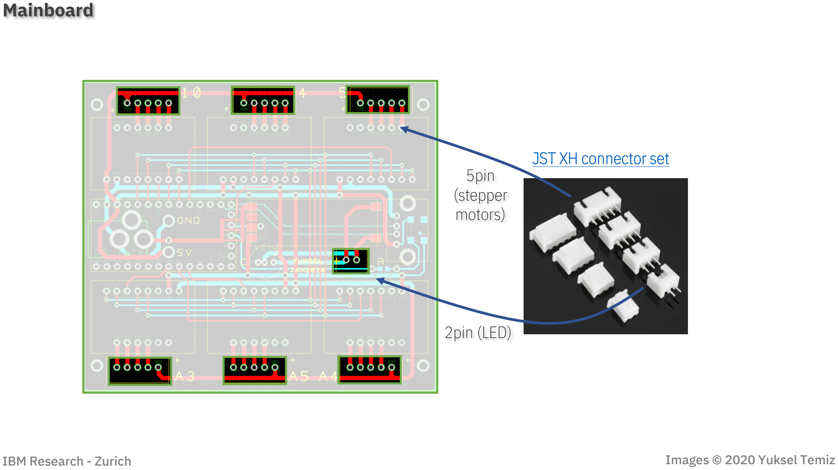
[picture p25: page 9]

JST XH connector set (https://www.banggood.com/40-Sets-JST-2_5mm-XH-2P-3P-4P-5Pin-Male-Female-Housing-Connector-with-Crimps-p-1180083.html?rmmds=myorder&cur_warehouse=CN)
5pin
(stepper
motors)

2pin (LED)

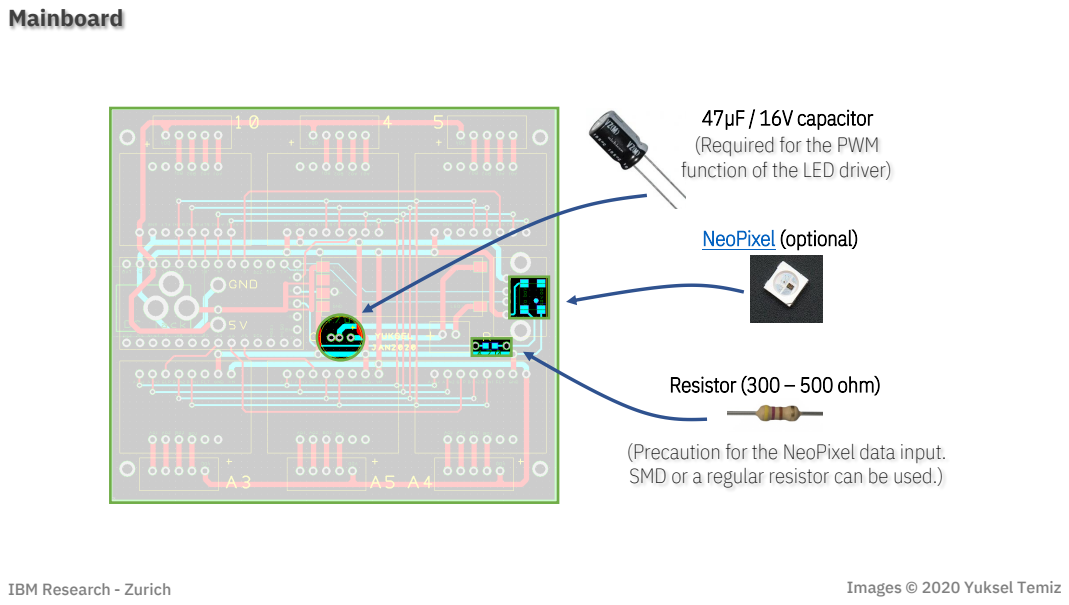
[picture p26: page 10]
NeoPixel (optional); Resistor (300 – 500 ohm)

47µF / 16V capacitor
(Required for the PWM
function of the LED driver)

(Precaution for the NeoPixel data input.
SMD or a regular resistor can be used.)

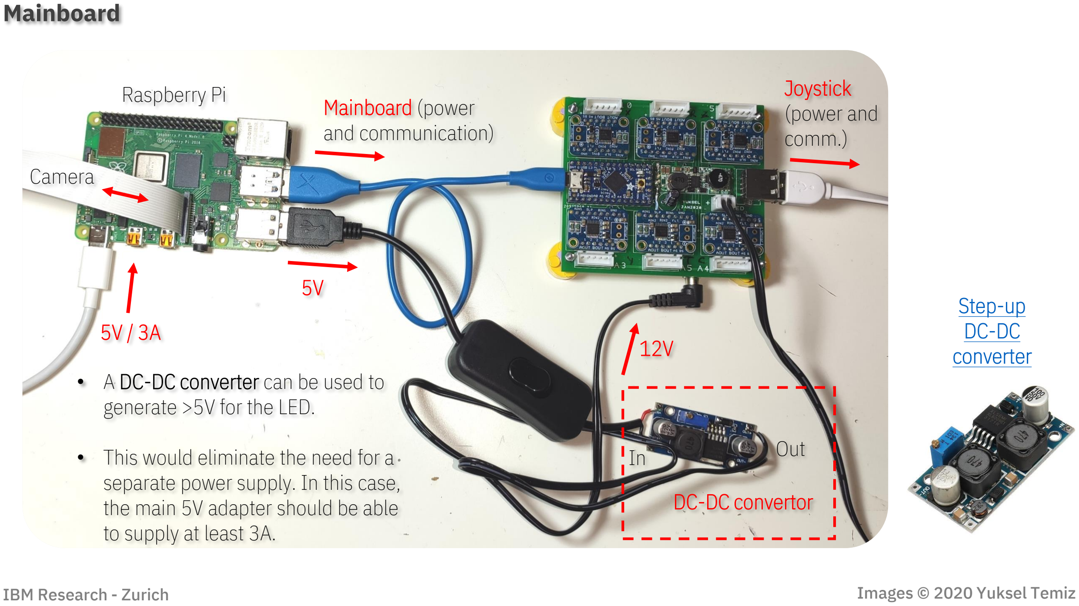
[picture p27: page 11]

5V / 3A

Mainboard (power
and communication)

Camera

5V

12V

DC-DC convertor

- A DC-DC converter can be used to generate >5V for the LED.
- This would eliminate the need for a separate power supply. In this case, the main 5V adapter should be able to supply at least 3A.

Step-up
DC-DC
converter (https://www.banggood.com/DC-DC-Boost-Buck-Adjustable-Step-Up-Step-Down-Automatic-Converter-XL6009-Module-p-1087346.html?rmmds=search&cur_warehouse=CN)

Joystick
(power and
comm.)
In | Out

Raspberry Pi

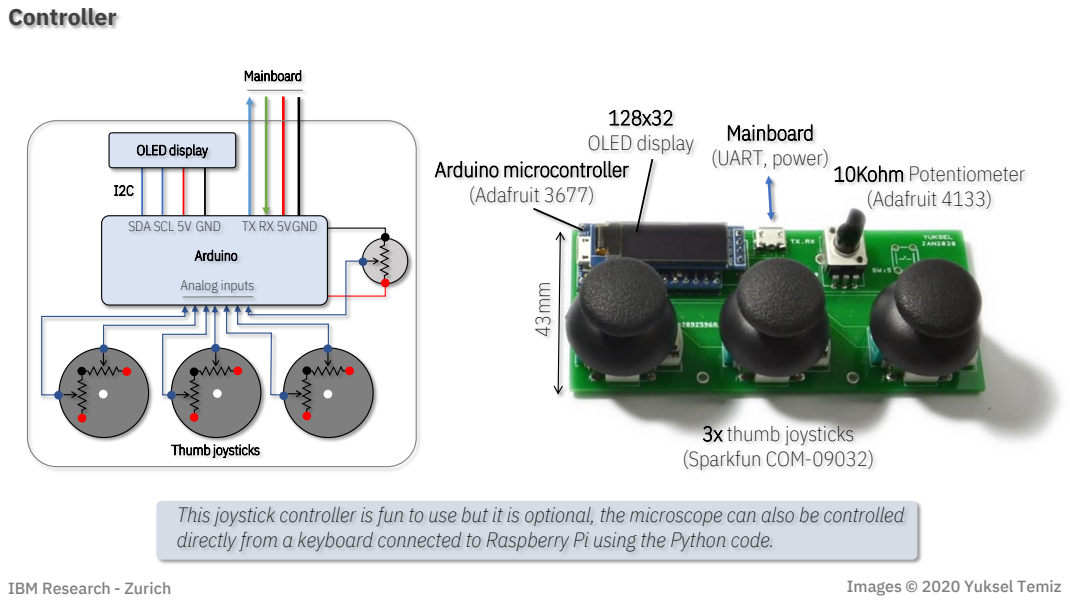
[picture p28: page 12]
Controller; 3x thumb joysticks (Sparkfun COM-09032); 10Kohm Potentiometer (Adafruit 4133); 128x32 OLED display Arduino microcontroller (Adafruit 3677); Mainboard (UART, power); Mainboard; Thumb joysticks; OLED display; SDA SCL; Arduino; 5V GND; GND; Analog inputs

This joystick controller is fun to use but it is optional, the microscope can also be controlled
directly from a keyboard connected to Raspberry Pi using the Python code.

IBM Research - Zurich

Images © 2020 Yuksel Temiz

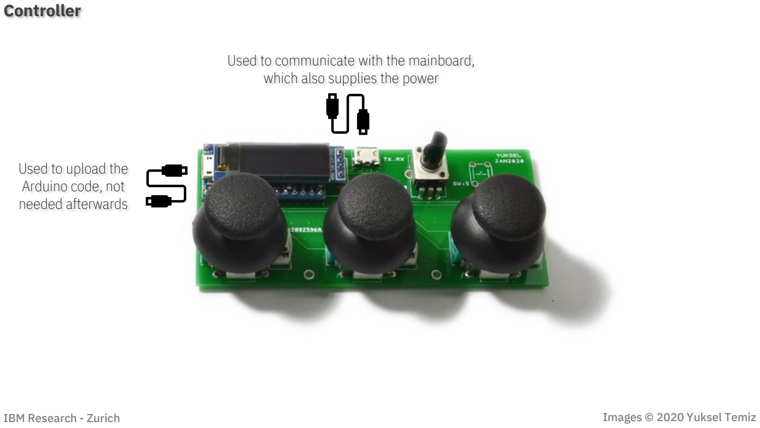
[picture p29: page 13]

Controller

Used to upload the
Arduino code, not
needed afterwards

Used to communicate with the mainboard, which also supplies the power

Controller

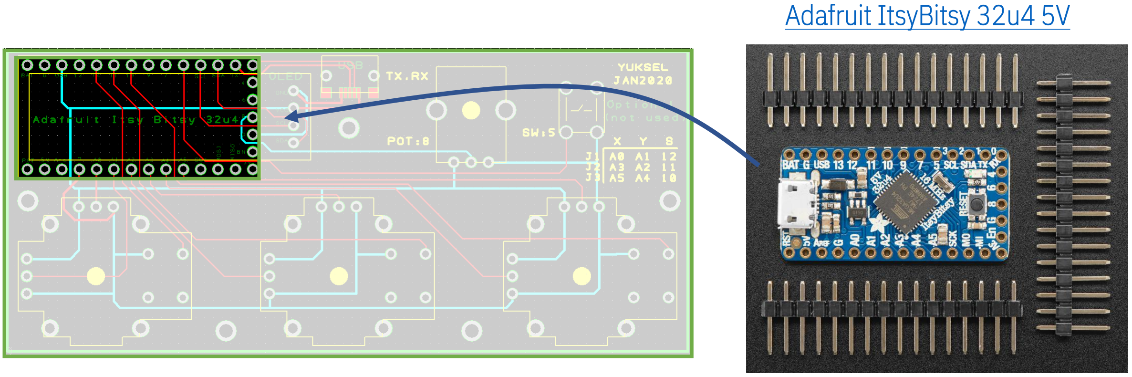
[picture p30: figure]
Adafruit ItsyBitsy 32u4 5V

Controller

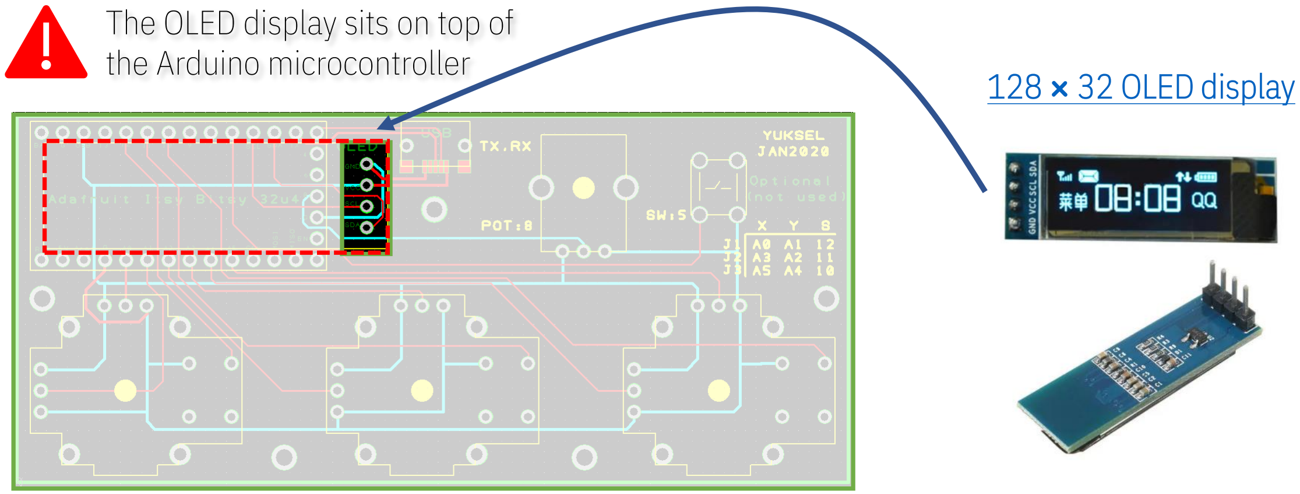
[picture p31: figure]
128 × 32 OLED display; The OLED display sits on top of the Arduino microcontroller
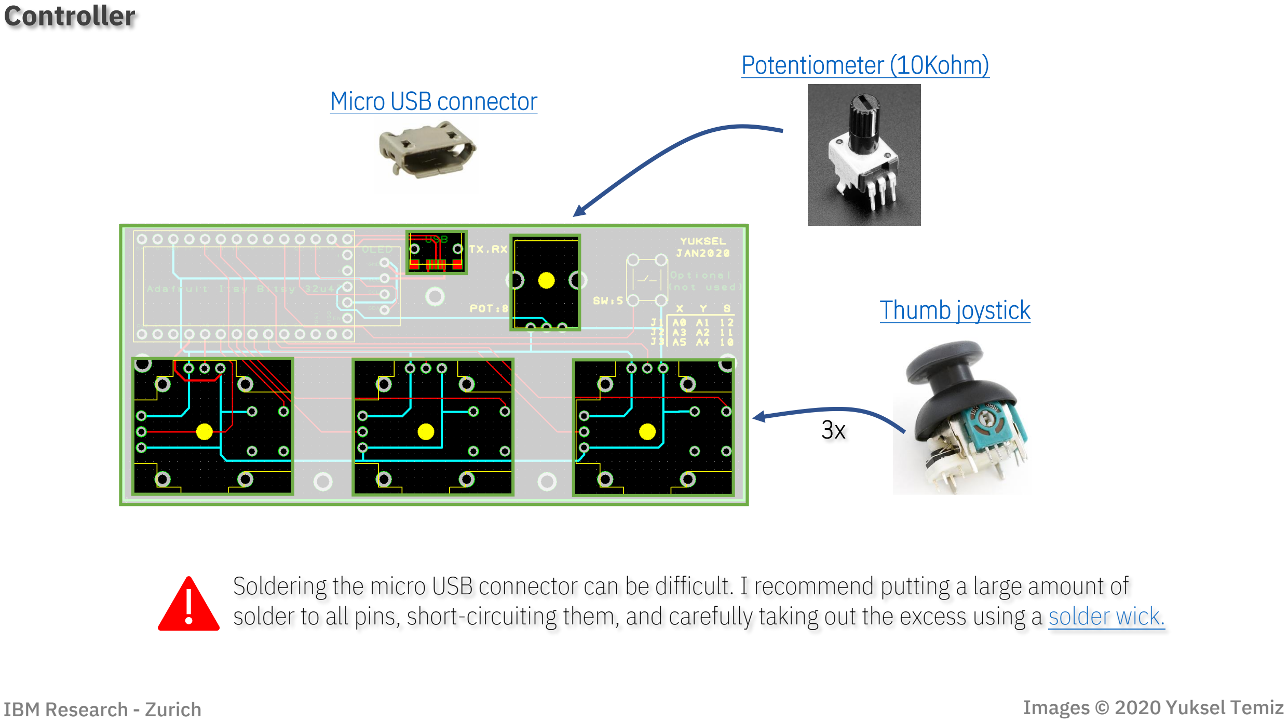
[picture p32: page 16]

Controller

Thumb joystick (https://www.sparkfun.com/products/9032)

3x

Potentiometer (10Kohm) (https://www.adafruit.com/product/4133)
Micro USB connector (https://www.digikey.com/products/en?keywords=609-4616-1-ND)

Soldering the micro USB connector can be difficult. I recommend putting a large amount of solder to all pins, short-circuiting them, and carefully taking out the excess using a solder wick. (https://www.banggood.com/3mm-Desoldering-Braid-Solder-Remover-Wick-Wire-p-982682.html?rmmds=buy&ID=6284394&cur_warehouse=CN)

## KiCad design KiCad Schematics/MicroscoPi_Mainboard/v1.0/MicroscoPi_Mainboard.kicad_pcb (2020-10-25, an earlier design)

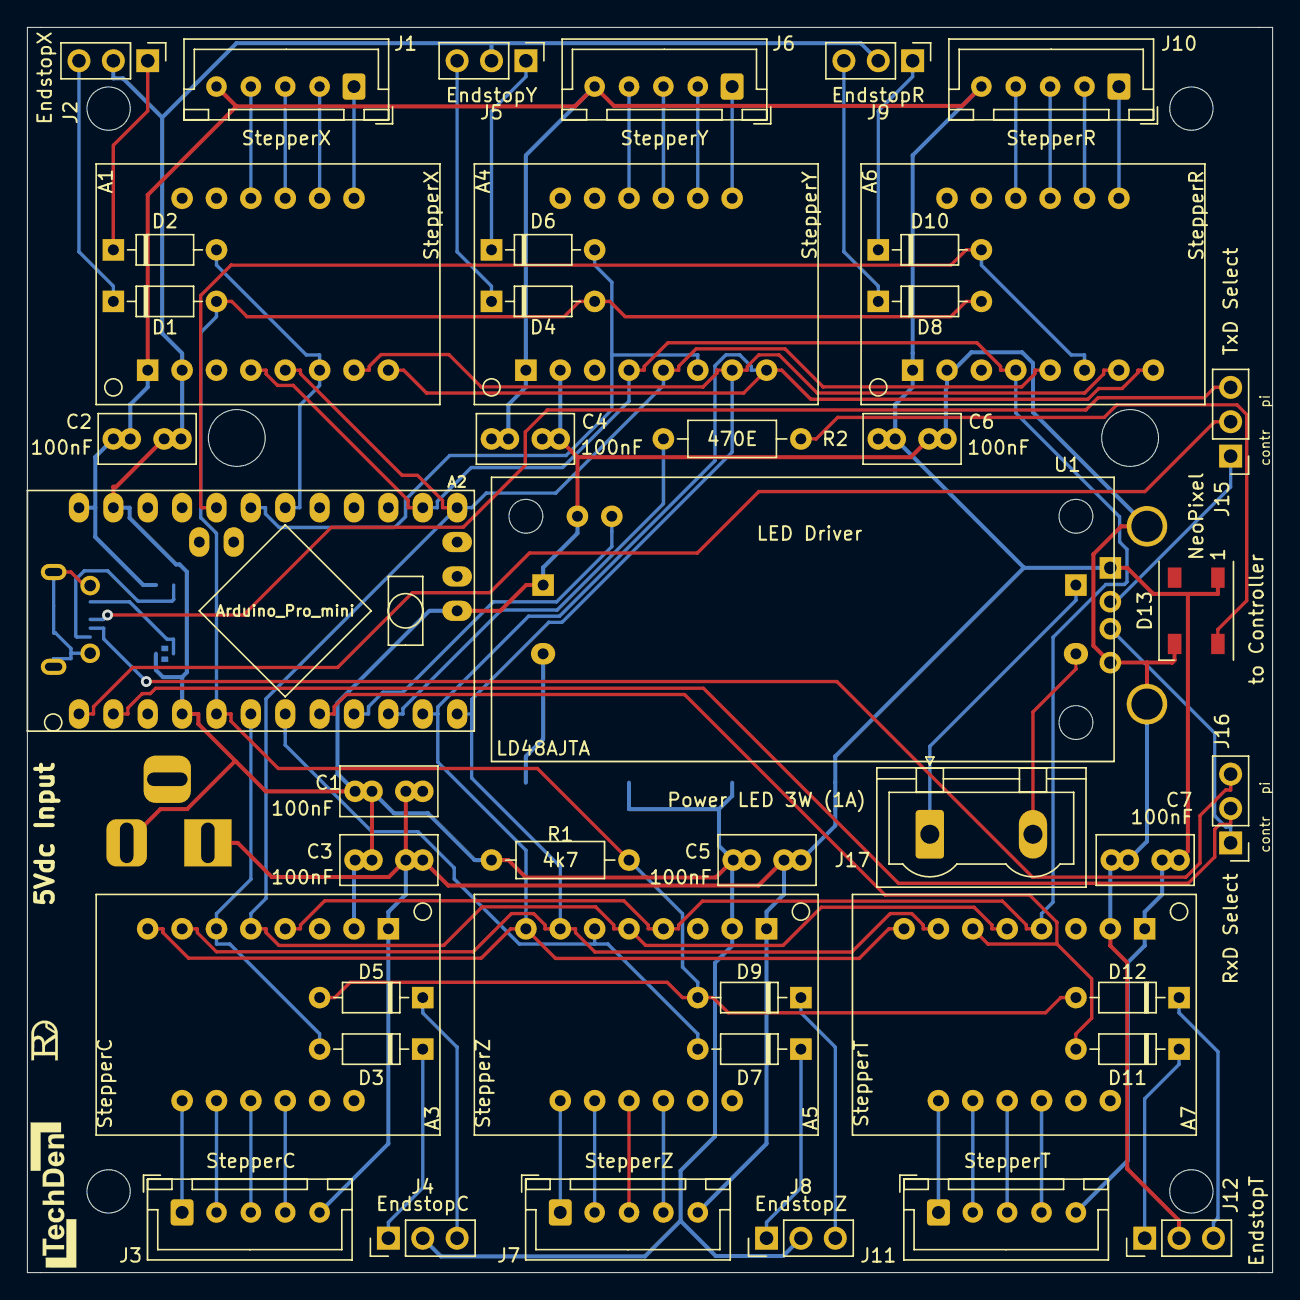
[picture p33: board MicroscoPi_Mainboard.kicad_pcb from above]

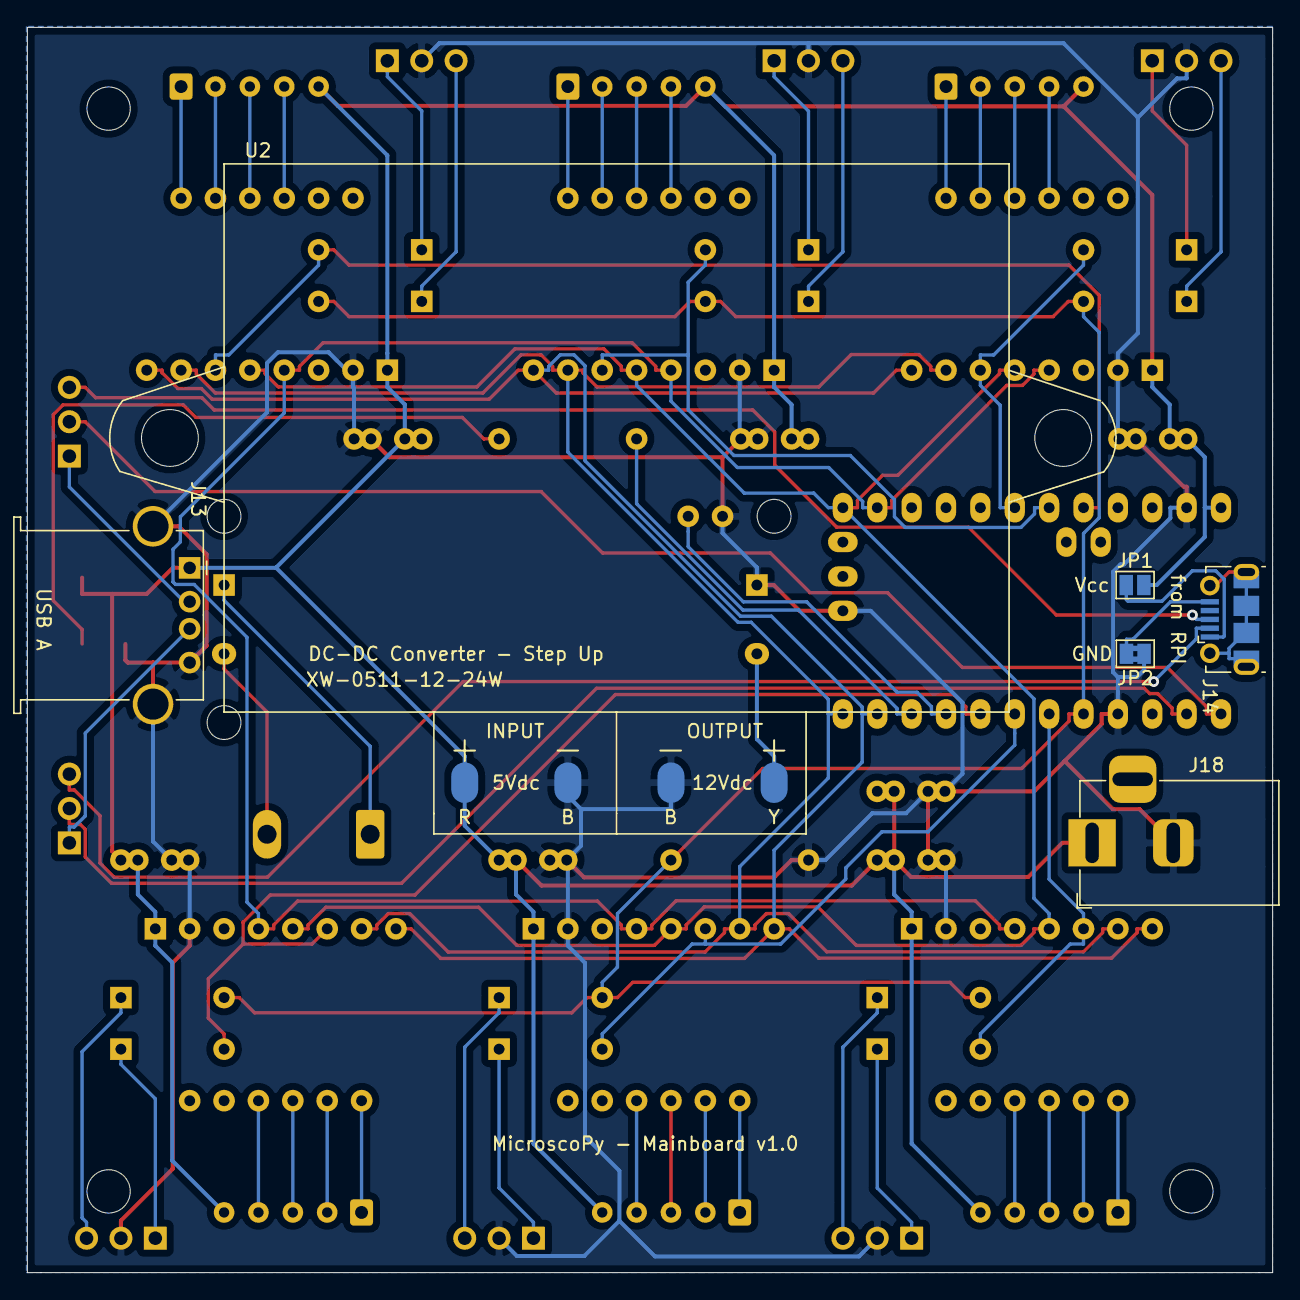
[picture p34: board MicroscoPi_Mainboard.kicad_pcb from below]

Board: 2 copper layers, 92.0 x 92.0 mm, 53 parts (6 on the bottom side), 63 nets.

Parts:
A1: StepperX; Adafruit_Breakout_DRV8825
A2: Arduino_Pro_mini; Arduino_pro_mini_v2
A3: StepperC; Adafruit_Breakout_DRV8825
A4: StepperY; Adafruit_Breakout_DRV8825
A5: StepperZ; Adafruit_Breakout_DRV8825
A6: StepperR; Adafruit_Breakout_DRV8825
A7: StepperT; Adafruit_Breakout_DRV8825
C1, C2, C3, C4, C5, C6, C7: 100nF; C_Rect_L7.0mm_W3.5mm_P2.50mm_P5.00mm
D1, D2, D3, D4, D5, D6, D7, D8, D9, D10, D11, D12: DUS; D_DO-35_SOD27_P7.62mm_Horizontal
D13: WS2812B; LED_WS2812B_PLCC4_5.0x5.0mm_P3.2mm
J1: StepperX; JST_XH_B5B-XH-A_1x05_P2.54mm_Vertical
J2: EndstopX; PinHeader_1x03_P2.54mm_Vertical
J3: StepperC; JST_XH_B5B-XH-A_1x05_P2.54mm_Vertical
J4: EndstopC; PinHeader_1x03_P2.54mm_Vertical
J5: EndstopY; PinHeader_1x03_P2.54mm_Vertical
J6: StepperY; JST_XH_B5B-XH-A_1x05_P2.54mm_Vertical
J7: StepperZ; JST_XH_B5B-XH-A_1x05_P2.54mm_Vertical
J8: EndstopZ; PinHeader_1x03_P2.54mm_Vertical
J9: EndstopR; PinHeader_1x03_P2.54mm_Vertical
J10: StepperR; JST_XH_B5B-XH-A_1x05_P2.54mm_Vertical
J11: StepperT; JST_XH_B5B-XH-A_1x05_P2.54mm_Vertical
J12: EndstopT; PinHeader_1x03_P2.54mm_Vertical
J13: USB A; USB_A_Stewart_SS-52100-001_Horizontal
J14: from RPI; USB_Micro-B_Molex-105017-0001
J15: TxD Select; PinHeader_1x03_P2.54mm_Vertical
J16: RxD Select; PinHeader_1x03_P2.54mm_Vertical
J17: Power LED 3W (1A); PhoenixContact_GMSTBVA_2,5_2-G-7,62_1x02_P7.62mm_Vertical
J18: Power Jack; BarrelJack_Horizontal
JP1: Vcc; SolderJumper-2_P1.3mm_Open_Pad1.0x1.5mm
JP2: GND; SolderJumper-2_P1.3mm_Bridged2Bar_Pad1.0x1.5mm
L1: Logo-TechDen; TechDen Logo - inverted
L2: Logo-RvD; RvD Logo inverted small
R1: 4k7; R_Axial_DIN0207_L6.3mm_D2.5mm_P10.16mm_Horizontal
R2: 470E; R_Axial_DIN0207_L6.3mm_D2.5mm_P10.16mm_Horizontal
U1: LD48AJTA
U2: XW-0511-12-24W

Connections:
+12V: U1.2, U2.4
/GPIO02: A2.5, D1.2, D4.2, D5.2, D8.2, D9.2, D12.2, R1.1
/GPIO03: A2.6, A3.6, D3.2
/GPIO04: A2.7, A5.6, D7.2
/GPIO05: A2.8, A7.6, D11.2
/GPIO06: A2.9, U1.6
/GPIO07: A2.10, R2.1
/GPIO08: A1.8, A2.11, A3.8, A4.8, A5.8, A6.8, A7.8
/GPIO09: A1.7, A2.12, A3.7, A4.7, A5.7, A6.7, A7.7
/GPIO10: A1.5, A2.13, A3.5, A4.5, A5.5, A6.5, A7.5
/GPIO11: A1.4, A2.14, A3.4, A4.4, A5.4, A6.4, A7.4
/GPIOA1: A1.6, A2.18, D2.2
/GPIOA2: A2.19, A4.6, D6.2
/GPIOA3: A2.20, A6.6, D10.2
/RxD: A2.2, J16.2
/RxD_Contr: J13.3, J16.1
/RxD_RPI: J14.2, J16.3
/TxD: A2.1, J15.2
/TxD_Contr: J13.2, J15.1
/TxD_RPI: J14.3, J15.3
GND: A1.2, A2.4, A2.23, A2.35, A3.2, A4.2, A5.2, A6.2, A7.2, C1.2, C2.2, C3.2, C4.2, C5.2, C6.2, C7.2, D13.3, J2.2, J4.2, J5.2, J8.2, J9.2, J12.2, J13.4, J13.5, J18.2, JP2.1, R1.2, U1.1, U1.5, U2.2, U2.3
unnamed: A1.10, J1.1
unnamed: A1.11, J1.2
unnamed: A1.12, J1.3
unnamed: A1.13, J1.4
unnamed: A3.10, J3.1
unnamed: A3.11, J3.2
unnamed: A3.12, J3.3
unnamed: A3.13, J3.4
unnamed: A4.10, J6.1
unnamed: A4.11, J6.2
unnamed: A4.12, J6.3
unnamed: A4.13, J6.4
unnamed: A5.10, J7.1
unnamed: A5.11, J7.2
unnamed: A5.12, J7.3
unnamed: A5.13, J7.4
unnamed: A6.10, J10.1
unnamed: A6.11, J10.2
unnamed: A6.12, J10.3
unnamed: A6.13, J10.4
unnamed: A7.10, J11.1
unnamed: A7.11, J11.2
unnamed: A7.12, J11.3
unnamed: A7.13, J11.4
unnamed: D1.1, J2.3
unnamed: D2.1, J2.1
unnamed: D3.1, J4.1
unnamed: D4.1, J5.3
unnamed: D5.1, J4.3
unnamed: D6.1, J5.1
unnamed: D7.1, J8.1
unnamed: D8.1, J9.3
unnamed: D9.1, J8.3
unnamed: D10.1, J9.1
unnamed: D11.1, J12.1
unnamed: D12.1, J12.3
unnamed: D13.4, R2.2
unnamed: J14.1, JP1.1
unnamed: J14.5, JP2.2
unnamed: J17.1, U1.3
unnamed: J17.2, U1.4
VCC: A1.1, A2.24, A3.1, A4.1, A5.1, A6.1, A7.1, C1.1, C2.1, C3.1, C4.1, C5.1, C6.1, C7.1, D13.1, J1.5, J3.5, J6.5, J7.5, J10.5, J11.5, J13.1, J18.1, JP1.2, U2.1

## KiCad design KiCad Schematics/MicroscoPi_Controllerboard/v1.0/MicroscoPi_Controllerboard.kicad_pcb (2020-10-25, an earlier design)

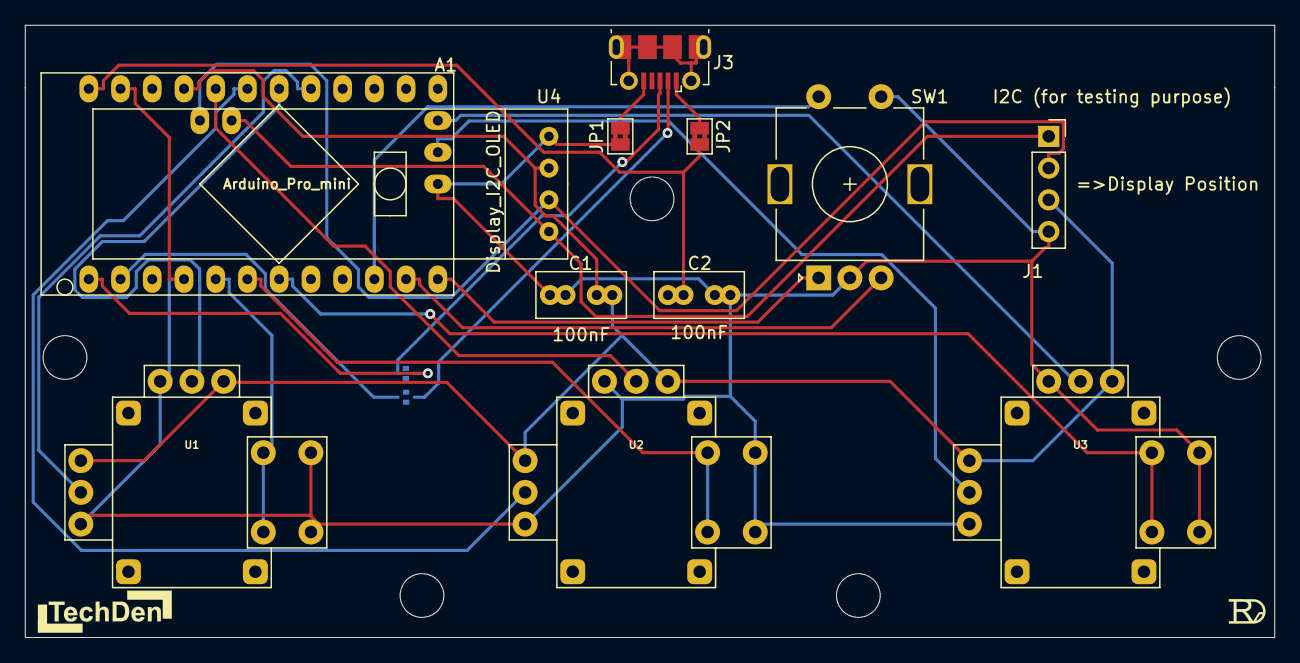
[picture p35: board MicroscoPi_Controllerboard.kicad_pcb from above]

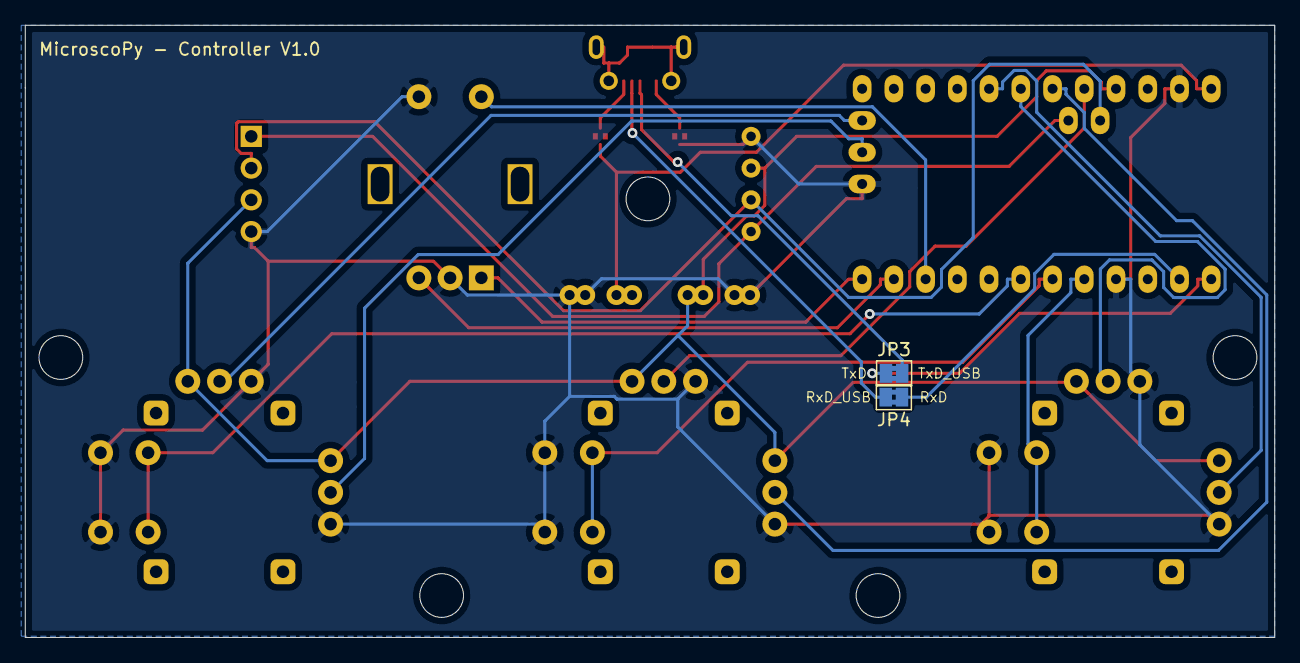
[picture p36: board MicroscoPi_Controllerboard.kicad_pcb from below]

Board: 2 copper layers, 100.0 x 49.0 mm, 16 parts (2 on the bottom side), 23 nets.

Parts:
A1: Arduino_Pro_mini; Arduino_pro_mini_v2
C1, C2: 100nF; C_Rect_L7.0mm_W3.5mm_P2.50mm_P5.00mm
J1: I2C (for testing purpose); PinSocket_1x04_P2.54mm_Vertical
J3: Power in; USB_Micro-B_Molex-105017-0001
JP1, JP2, JP3, JP4: SolderJumper_2_Bridged; SolderJumper-2_P1.3mm_Bridged2Bar_Pad1.0x1.5mm
L1: Logo-TechDen; TechDen Logo - inverted
L2: Logo-RvD; RvD Logo inverted small
SW1: Rotary_Encoder_Switch; RotaryEncoder_Alps_EC11E-Switch_Vertical_H20mm
U1, U2, U3: JOYSTICK_BUTTON; Joystick_w_Button
U4: Display_I2C_OLED; SSD1306_OLED-0.91-128x32

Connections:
+5V: A1.21, C1.1, J1.3, U1.X1, U1.Y1, U2.X1, U2.Y1, U3.X1, U3.Y1, U4.3
/BUTTON1: A1.5, U1.SWa
/BUTTON2: A1.6, U2.SWa
/BUTTON3: A1.7, U3.SWa
/BUTTON4: A1.10, SW1.S2
/C: A1.20, U2.X2
/CLK: A1.12, SW1.A
/DT: A1.11, SW1.B
/GPIOA0: A1.17, U1.Y2
/GPIOA1: A1.18, U1.X2
/GPIOA2: A1.19, U2.Y2
/GPIOA6: A1.34, U3.Y2
/GPIOA7: A1.33, U3.X2
/RxD: A1.2, JP4.1
/RxD_USB: J3.2, JP4.2
/SCL: A1.31, J1.2, U4.2
/SDA: A1.32, J1.1, U4.1
/TxD: A1.1, JP3.2
/TxD_USB: J3.3, JP3.1
GND: A1.4, A1.23, A1.35, C1.2, C2.2, J1.4, JP1.2, SW1.C, SW1.S1, U1.SWb, U1.X3, U1.Y3, U2.SWb, U2.X3, U2.Y3, U3.SWb, U3.X3, U3.Y3, U4.4
unnamed: J3.1, JP2.1
unnamed: J3.5, JP1.1
VCC: A1.24, C2.1, JP2.2

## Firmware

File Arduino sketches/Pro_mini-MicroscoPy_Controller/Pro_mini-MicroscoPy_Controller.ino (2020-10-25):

/* This code sends data via UART from one Arduino board (controller) to another (MainBoard) to control the stepper motors and the LED illumination
 * Arduino sends the data only if there is a change in the value of the joysticks or the LED potentiometer 
 * Therefore, there is no continuous data communication between the mainboard and the controller
 * Board: Arduino Pro mini 
 */

#include <Wire.h> // needed for the I2C communication of the OLED, already installed in Arduino IDE
#include <Adafruit_GFX.h> // needed for the OLED // Copyright (c) 2012 Adafruit Industries.  All rights reserved.
#include <Adafruit_SSD1306.h> // needed for the OLED // Copyright (c) 2012 Adafruit Industries.  All rights reserved.

// Arduino pins for the joysticks
#define joystickX A1
#define joystickY A0
#define joystickZ A2
#define joystickC A3
#define joystickR A7
#define joystickT A6
#define BUTTON1 2 //Button Joystick U1
#define BUTTON2 3 //Button Joystick U2 
#define BUTTON3 4 //Button Joystick U3 
#define RE_DT 8  // Rotary encoder signal DT (output A)
#define RE_CLK 9  // Rotary encoder signal CLK (output B)
#define RE_BUTTON 7 // Rotary encoder button | active LOW
#define BUTTON4 RE_BUTTON // ... also known as BUTTON4
#define RE_MAX 40 // Count value of one rotation of the   Rotary encoder

// potentiometer for the LED intensity
//#define potLED 8

// change these values to set the direction of the movement with respect to the joystick
// the direction can also be changed by simply rotating the motor 180-deg 

#define directionX -1
#define directionY 1
#define directionZ 1
#define directionC 1
#define directionR 1
#define directionT 1

// the joystick has a variable speed control at 3 predefined speeds
// change these values to change the speed of the motor

#define fast 500
#define medium 50
#define slow 10
//#define SCREEN_WIDTH 128 // OLED display width, in pixels
//#define SCREEN_HEIGHT 32 // OLED display height, in pixels

//Adafruit_SSD1306 display(SCREEN_WIDTH, SCREEN_HEIGHT, &Wire);
#define OLED_RESET -1
Adafruit_SSD1306 display(OLED_RESET);

#define TUNE_X 900
#define TUNE_Y 900
#define TUNE_C 900
#define TUNE_Z 900
#define TUNE_R 900
#define TUNE_T 900
#define TUNE_L 1023
#define LONGPRESSTIME 2000

int readX;
int readY;
int readC;
int readZ;
int readR;
int readT;
int readL;

bool button1Active = false;
long button1Timer;
bool longPress1Active = false;
bool button2Active = false;
long button2Timer;
bool longPress2Active = false;
bool button3Active = false;
long button3Timer;
bool longPress3Active = false;
bool button4Active = false;
long button4Timer;
bool longPress4Active = false;

int readXlast = 0;
int readYlast = 0;
int readClast = 0;
int readZlast = 0;
int readRlast = 0;
int readTlast = 0;
int readLlast = 0;
bool homingLast = 0;
int RE_counter = 0; // Rotary encoder counter
int RE_state; // Rotary encoder counter state
int RE_lastState; // Rotary encoder counter last state

String stepper;

void setup() {

  display.begin(SSD1306_SWITCHCAPVCC, 0x3c); //initialize the display
  Serial.begin(57600); //start the serial communication, Serial: UART
//  Serial.println("starting up MicroscoPy Controller"); 
//  analogReference(EXTERNAL); // use AREF for reference voltage connected to +5V Power
  
  pinMode(joystickX, INPUT); // X stepper
  pinMode(joystickY, INPUT); // Y stepper
  pinMode(joystickZ, INPUT); // Z stepper
  pinMode(joystickC, INPUT); // Focus stepper
  pinMode(joystickR, INPUT); // Rotatie stepper
  pinMode(joystickT, INPUT); // Tilt stepper
  pinMode(BUTTON1, INPUT_PULLUP); //Joystick X/Y button | active LOW
  pinMode(BUTTON2, INPUT_PULLUP); //Joystick Z/C button | active LOW
  pinMode(BUTTON3, INPUT_PULLUP); //Joystick R/T button | active LOW 
  pinMode(BUTTON4, INPUT_PULLUP);  //Rotary encoder button | active LOW
  pinMode (RE_DT,INPUT_PULLUP); // Rotary encoder DT signal
  pinMode (RE_CLK,INPUT_PULLUP); // Rotary encoder CLK signal
//  pinMode(potLED, INPUT);

// show a start-up text on the OLED display
  display.clearDisplay();
  display.setRotation(2);
  display.setTextColor(WHITE);
  display.setCursor(0, 10);
  display.setTextSize(2);
  display.println("Starting");
  display.display();

  delay(2000); //delay for the start-up message

// set the LED illumination to the Rotary encoder value at the start-up

//  readLlast = map((analogRead(potLED)), 0, 1023, 0, 20); // map to 20 steps (5% steps) 
  readLlast = map(read_RE(), 0, RE_MAX, 0, 20) ; // map to 20 steps (5% steps)
  Serial.print(readL); Serial.print("L"); Serial.print(","); // send the data to the MainBoard to update the LED intensity
  
// show the LED intensity on the OLED display

  display.clearDisplay();
  display.setCursor(0, 10);
  display.setTextSize(2);
//  display.print("LED:"); display.print(100 - (readLlast * 5)); display.print("%"); // PWM of the LED driver used in the prototype works in the opposite direction
  display.print("LED: "); display.print(readLlast * 5); display.print("%");
  display.display();

   // Reads the initial state of the outputA
//   RE_lastState = digitalRead(RE_CLK);
}

void loop() {

  readX = map((analogRead(joystickX)), 0, TUNE_X, -3, 3); // map the measured value to 3 positive and 3 negative speed values
//  readX=0; // disabled
//  readX = analogRead(joystickX); // map the measured value to 3 positive and 3 negative speed values
//  Serial.println(readX);
  if ((readX != readXlast) ) { //check if it has changed
    if (readX == -3) {
      Serial.print(fast * -1 * directionX); Serial.print("X"); Serial.print(",");
      readXlast = readX;
    }
    if (readX == -2)  {
      Serial.print(medium * -1 * directionX); Serial.print("X"); Serial.print(",");
      readXlast = readX;
    }
    if (readX == -1)  {
      Serial.print(slow * -1 * directionX); Serial.print("X"); Serial.print(",");
      readXlast = readX;
    }
    if (readX == 0) {
      Serial.print(0); Serial.print("O"); Serial.print(","); //stop the stepper motor by sending "0O,"
      readXlast = readX;
    }
    if (readX == 1)  {
      Serial.print(slow * directionX); Serial.print("X"); Serial.print(",");
      readXlast = readX;
    }

    if (readX == 2)  {
      Serial.print(medium * directionX); Serial.print("X"); Serial.print(",");
      readXlast = readX;
    }

    if (readX == 3)  {
      Serial.print(fast * directionX); Serial.print("X"); Serial.print(",");
      readXlast = readX;
    }
  }

// REPEAT THE SAME FOR ALL OTHER JOYSTICK POTENTIOMETERS 

  readY = map((analogRead(joystickY)), 0, TUNE_Y, -3, 3);
//  readY=0; // disabled
  if (readY != readYlast) {
    if (readY == -3)  {
      Serial.print(fast * -1 * directionY); Serial.print("Y"); Serial.print(",");
      readYlast = readY;
    }
    if (readY == -2)  {
      Serial.print(medium * -1 * directionY); Serial.print("Y"); Serial.print(",");
      readYlast = readY;
    }
    if (readY == -1)  {
      Serial.print(slow * -1 * directionY); Serial.print("Y"); Serial.print(",");
      readYlast = readY;
    }
    if (readY == 0) {
      Serial.print(0); Serial.print("O"); Serial.print(",");
      readYlast = readY;
    }
    if (readY == 1)  {
      Serial.print(slow * directionY); Serial.print("Y"); Serial.print(",");
      readYlast = readY;
    }

    if (readY == 2)  {
      Serial.print(medium * directionY); Serial.print("Y"); Serial.print(",");
      readYlast = readY;
    }

    if (readY == 3)  {
      Serial.print(fast * directionY); Serial.print("Y"); Serial.print(",");
      readYlast = readY;
    }
  }

  readC = map((analogRead(joystickC)), 0, TUNE_C, -3, 3);
//  readC=0; // disabled
  if (readC != readClast) {
    if (readC == -3)  {
      Serial.print(fast * -1 * directionC); Serial.print("C"); Serial.print(",");
      readClast = readC;
    }
    if (readC == -2)  {
      Serial.print(medium * -1 * directionC); Serial.print("C"); Serial.print(",");
      readClast = readC;
    }
    if (readC == -1) {
      Serial.print(slow * -1 * directionC); Serial.print("C"); Serial.print(",");
      readClast = readC;
    }
    if (readC == 0)  {
      Serial.print(0); Serial.print("O"); Serial.print(",");
      readClast = readC;
    }
    if (readC == 1)  {
      Serial.print(slow * directionC); Serial.print("C"); Serial.print(",");
      readClast = readC;
    }

    if (readC == 2)  {
      Serial.print(medium * directionC); Serial.print("C"); Serial.print(",");
      readClast = readC;
    }

    if (readC == 3) {
      Serial.print(fast * directionC); Serial.print("C"); Serial.print(",");
      readClast = readC;
    }
  }

  readZ = map((analogRead(joystickZ)), 0, TUNE_Z, -3, 3);
//  readZ=0; // disabled
  if (readZ != readZlast) {
    if (readZ == -3)  {
      Serial.print(fast * -1 * directionZ); Serial.print("Z"); Serial.print(",");
      readZlast = readZ;
    }
    if (readZ == -2)  {
      Serial.print(medium * -1 * directionZ); Serial.print("Z"); Serial.print(",");
      readZlast = readZ;
    }
    if (readZ == -1)  {
      Serial.print(slow * -1 * directionZ); Serial.print("Z"); Serial.print(",");
      readZlast = readZ;
    }
    if (readZ == 0) {
      Serial.print(0); Serial.print("O"); Serial.print(",");
      readZlast = readZ;
    }
    if (readZ == 1) {
      Serial.print(slow * directionZ); Serial.print("Z"); Serial.print(",");
      readZlast = readZ;
    }

    if (readZ == 2)  {
      Serial.print(medium * directionZ); Serial.print("Z"); Serial.print(",");
      readZlast = readZ;
    }

    if (readZ == 3)  {
      Serial.print(fast * directionZ); Serial.print("Z"); Serial.print(",");
      readZlast = readZ;
    }
  }

  readR = map((analogRead(joystickR)), 0, TUNE_R, -3, 3); 
//  readR=0; // disabled
  if (readR != readRlast)  {
    if (readR == -3) {
      Serial.print(fast * -1 * directionR); Serial.print("R"); Serial.print(",");
      readRlast = readR;
    }
    if (readR == -2) {
      Serial.print(medium * -1 * directionR); Serial.print("R"); Serial.print(",");
      readRlast = readR;
    }
    if (readR == -1)  {
      Serial.print(slow * -1 * directionR); Serial.print("R"); Serial.print(",");
      readRlast = readR;
    }
    if (readR == 0) {
      Serial.print(0); Serial.print("O"); Serial.print(",");
      readRlast = readR;
    }
    if (readR == 1)  {
      Serial.print(slow * directionR); Serial.print("R"); Serial.print(",");
      readRlast = readR;
    }

    if (readR == 2)  {
      Serial.print(medium * directionR); Serial.print("R"); Serial.print(",");
      readRlast = readR;
    }

    if (readR == 3) {
      Serial.print(fast * directionR); Serial.print("R"); Serial.print(",");
      readRlast = readR;
    }
  }

  readT = map((analogRead(joystickT)), 0, TUNE_T, -3, 3);
//  readT=0; // disabled
  if (readT != readTlast)  {
    if (readT == -3) {
      Serial.print(fast * -1 * directionT); Serial.print("T"); Serial.print(",");
      readTlast = readT;
    }
    if (readT == -2) {
      Serial.print(medium * -1 * directionT); Serial.print("T"); Serial.print(",");
      readTlast = readT;
    }
    if (readT == -1) {
      Serial.print(slow * -1 * directionT); Serial.print("T"); Serial.print(",");
      readTlast = readT;
    }
    if (readT == 0)  {
      Serial.print(0); Serial.print("O"); Serial.print(",");
      readTlast = readT;
    }
    if (readT == 1)  {
      Serial.print(slow * directionT); Serial.print("T"); Serial.print(",");
      readTlast = readT;
    }

    if (readT == 2)  {
      Serial.print(medium * directionT); Serial.print("T"); Serial.print(",");
      readTlast = readT;
    }

    if (readT == 3)  {
      Serial.print(fast * directionT); Serial.print("T"); Serial.print(",");
      readTlast = readT;
    }
  }
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

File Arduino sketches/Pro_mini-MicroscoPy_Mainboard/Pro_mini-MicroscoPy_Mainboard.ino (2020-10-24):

/* This code controls the stepper motors and the LED intensity
   according to the data received from the UART (RX, TX) (Controller) or the USB (e.g. Raspberry Pi)
   All 6 motors share the same stepper motor pins, but only one
   is activated depending on the status of the Enable pin of the driver
   Data format: "50X," where 50 is the speed and X is the axis
   X: X axis, Y: Y axis, Z: Z axis (magnification), C: camera stage (Focus), R: rotation, T: tilt
   d: Button1 ShortPressed, D Button1 LongPressed,
   e: Button2 ShortPressed, E Button2 LongPressed,
   f: Button3 ShortPressed, F Button3 LongPressed,
   g: Button4 ShortPressed, G Button4 LongPressed,
   The data is executed after a "," (comma) is received
   Hence; disconnect the TxD RxD pins (jumpers on PCB) when uploading a new sketch
*/

// board: Arduino Pro mini
// Stepper driver; Adafruit Breakoutboard DRV8825 from Aliexpress

#include <AccelStepper.h> // Library to control stepper motors // Copyright (C) 2010-2018 Mike McCauley
#include <Adafruit_NeoPixel.h> // Library to control the optional status LED
#include <EEPROM.h>

////////////////// Arduino pins connected to the EN of each stepper motor driver

#define TESTMODE false // In Testmode the endstops are disabled

// stepper motor pins
#define IN1 8  //B1 - pin3 stepper driver Breakoutboard
#define IN2 9  //B2 - pin4 stepper driver Breakoutboard
#define IN3 10 //A2 - pin5 stepper driver Breakoutboard
#define IN4 11 //A1 - pin6 stepper driver Breakoutboard
#define ENDSTOP 2 //Pin connected to Endstop switch boards

#define NEO_COUNT 1
#define NEOBLUE 50
#define NEOGREEN 50
#define NEORED 50

// motor enable pins
#define EnableX A1
#define EnableY A2
#define EnableR A3
#define EnableC 3
#define EnableZ 4
#define EnableT 5

// value 0 means no endstop
#if TESTMODE
#define homeDirX 0  // disable endstops
#define homeDirY 0
#define homeDirC 0
#define homeDirZ 0
#define homeDirR 0
#define homeDirT 0
#else
#define homeDirX 1 // Homing direction of X
#define homeDirY -1  // Homing direction of Y
#define homeDirC 1  // Homing direction of C
#define homeDirZ 1  // Homing direction of Z
#define homeDirR 0  // R has no endstop
#define homeDirT 1  // T has no endstop
#endif

#define CHECK 1
#define NO_CHECK 0

#define MAX_X 4500  // max X steps
#define MAX_Y 4000  // max Y steps
#define MAX_C 5500  // max C steps
#define MAX_Z 5050  // max Z steps
#define MAX_R 0  // max R steps
#define MAX_T 3400  // max T steps

#define LEDPWM 6 // High-power illumination LED PWM control pin
#define NEO_PIN 7 // GPIO-nr NeoPixel status LED | PWM output


#define PRESET1_Y 2110
#define PRESET1_X 2290
#define PRESET1_C 3820
#define PRESET1_Z 1200
#define PRESET1_R -1
#define PRESET1_T 3400
#define PRESET1_L 191


const int stepsPerRevolution = 2048; //set according to the specs of the stepper motor
String receivedString; //incoming data from the serial ports (USB or UART)
int stepperSpeed;
//position variables
long stepX = 0;
long stepY = 0;
long stepC = 0;
long stepZ = 0;
long stepR = 0;
long stepT = 0;
int laststepperMotor = "";
int lastspeedStepper = 0;
int stepDir;
int checkEndstops;
char stepperState; //variable to define the active stepper motor, X, Y, Z, C, R, T
int LEDintensity;
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

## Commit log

2020-10-25 The entire project
    [01-RackGear.stl, 02-MotorGear.stl, 03-MotorHousing.stl, 04-CameraAdapter.stl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]
2020-10-25 BOM lists added
    [MicroscoPi_Controllerboard_bom_V2.0.xlsx, MicroscoPi_Mainboard_bom_v2.0.xlsx]
